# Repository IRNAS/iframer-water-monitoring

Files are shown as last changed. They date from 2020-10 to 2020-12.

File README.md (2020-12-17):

# Ifremer water monitoring

## Introduction

This repository contains all documentation and source code required to setup either a Inductive Conductivity CTZN sensor (marked on sensor as SN-PCTZB) or Optical Dissolved Oxygen OPTOD sensor (marked on sensor as SN-PODOC).
Sensors product page can be found on manufacturers [website][product_page].
The source code was written to work on [B-L072Z-LRWAN1][lora_board], while using Arduino core.

All manufacturers documentation can be found in `aqualabo_docs` folder.
Desktop application for measuring can be found in `aqualabo_software` folder.

## Prerequisites
* B-L072Z-LRWAN1
* Pira Smart RS485 Add-On board, documentation about it can be found in `rs485_addon_hardware` folder
* CTZN sensor or OPTOD sensor
* Arduino library for [Modbus protocol][arduino_library]
* Aqualabo 4200 Digital Module box, needed only for finding ModBus address and calibration.

<p align="center">
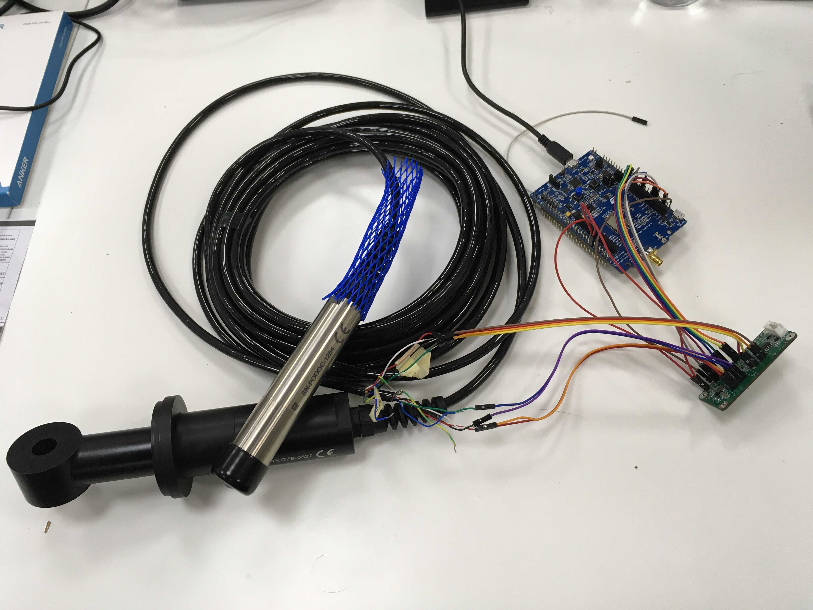
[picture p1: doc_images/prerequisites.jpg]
  <br><br>
  <i>Required setup</i><br>
</p>

[product_page]: https://en.aqualabo.fr/ctzn-digital-sensor-bare-wires-3-m-cable-stainless-steel-pipe-b4002.html
[lora_board]: https://www.st.com/en/evaluation-tools/b-l072z-lrwan1.html
[arduino_library]: https://github.com/4-20ma/ModbusMaster 

## Aqualabo sensors

This library currently supports two sensors:

* CTZN inductive conductivity sensor, address 50
* OPTOD optical oxygen sensor, address 10

## Finding ModBus address of the Aqualabo sensor

The best way to find address of Aqualabo sensor is to use Calsens software, installer for it can be found in `aqualabo_software` folder.
When using Calsens software the Aqualabo 4200 Digital Module box is required.

## Calibrating the Aqualabo sensor

To calibrate the Aqualabo sensor we have to use Calsens software, installer for it can be found in `aqualabo_software` folder.
Calibration procedure is described in user manuals of each specific sensors, as well as in `Modbus_Specifications_v021-EN.pdf` document.
When using Calsens software the Aqualabo 4200 Digital Module box is required.

## Wiring

There are two different wiring setups that need to be taken care of.

### Connections between Aqualabo sensor and Add-on board

As seen on image below Aqualabo sensor has 6 wires, wires numbers 2 (blue) and 6 (green/yellow) are not needed.
Aqualabo sensor has to be connected to one of two ports P1 or P2. Markings for Addon board can be seen on schematic below, there are also silkscreen markings on the bottom side of the board.

<p align="center">
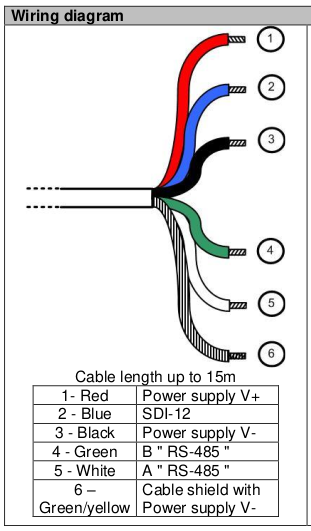
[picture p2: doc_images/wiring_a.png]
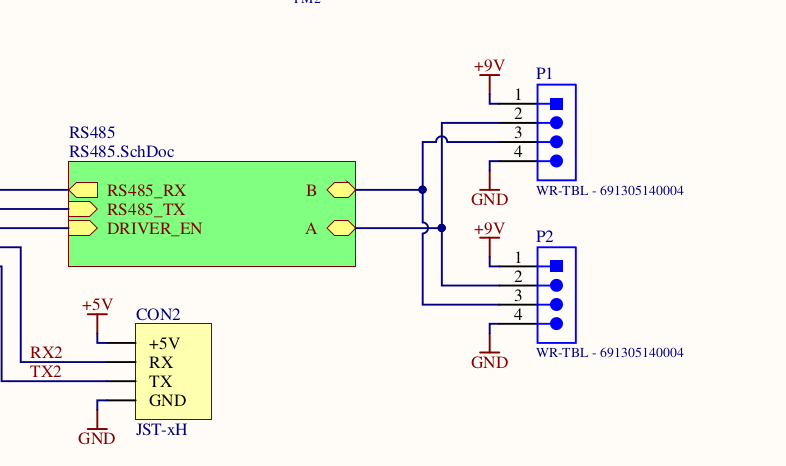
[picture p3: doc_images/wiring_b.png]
<br><br>
  <i>Wiring scheme of Aqualabo sensor and Add-on board</i><br>
</p>

### Connections between Add-on board and microcontroller

Connections are marked on image below, we need to provide following lines:
* 3.3V
* 5V
* GND
* TXD
* RXD
* GPIO18 (UART_SEL_B)
* GPIO23 (UART_SEL_A)
* GPIO24 (UART_INH)
* GPIO25 (DRIVER_EN)

**Important**: We actually do not need to switch UART lines when connection Add-on board to the microcontroller.
There is a mistake in naming in schematic and lines are already switched.
We therefore connect TX line from microcontroller to the TXD of Raspberry Pi header, same goes for RX and RXD.

<p align="center">
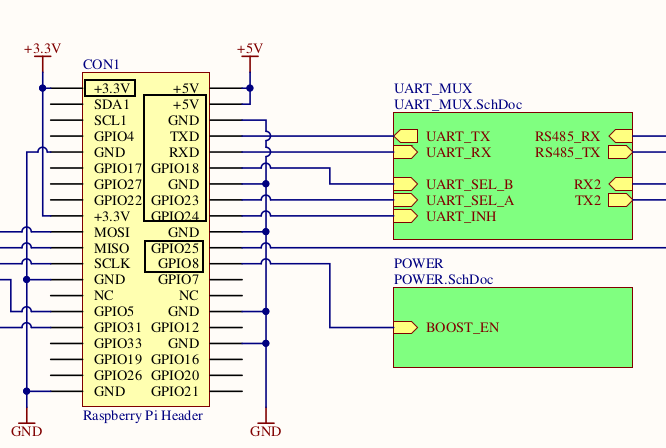
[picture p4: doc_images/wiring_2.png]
  <br><br>
  <i> Connections on Add-on board</i><br>
</p>

## Hardware changes on the Add-on board

There were some changes needed on the board to make communication possible.
This changes are not visible in schematic and are described here.

Changes:
* R7 0 ohm resistor should be placed
* R10 0 ohm resistor should not be placed
* R11 10 Kohm resistor should be replaced with 0 ohm resistor

Additional changes are needed to achieve low current consumption on Add-on V1 board:
* Remove chip U4 uart mux chip
* Connect together with a wire solder pads 1 and 3 left behind U4 chip.
* Connect together with a wire solder pads 12 and 13 left behind U4 chip.
* Solder on 3.3V low drop regulator and connect to its input 5V line, then connect to its output 3V line of the Add-on board.

For required connections refer to the image below.

<p align="center">
<br><br>
  <i> Low current consumption modifications on Add-on board</i><br>
</p>

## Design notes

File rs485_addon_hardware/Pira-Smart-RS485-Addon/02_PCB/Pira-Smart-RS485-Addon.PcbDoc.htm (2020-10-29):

Reporting Options

# File in Previous Format

Date | : | 16. 04. 2019
Time | : | 11:17:16
Filename | : | D:\OneDrive\IRNAS-Common\_NEW-IRNAS-COMMON\Pira-Smart-RS485-Addon\02_PCB\Pira-Smart-RS485-Addon.PcbDoc

Version | Warning

This file was generated by an earlier version of the software

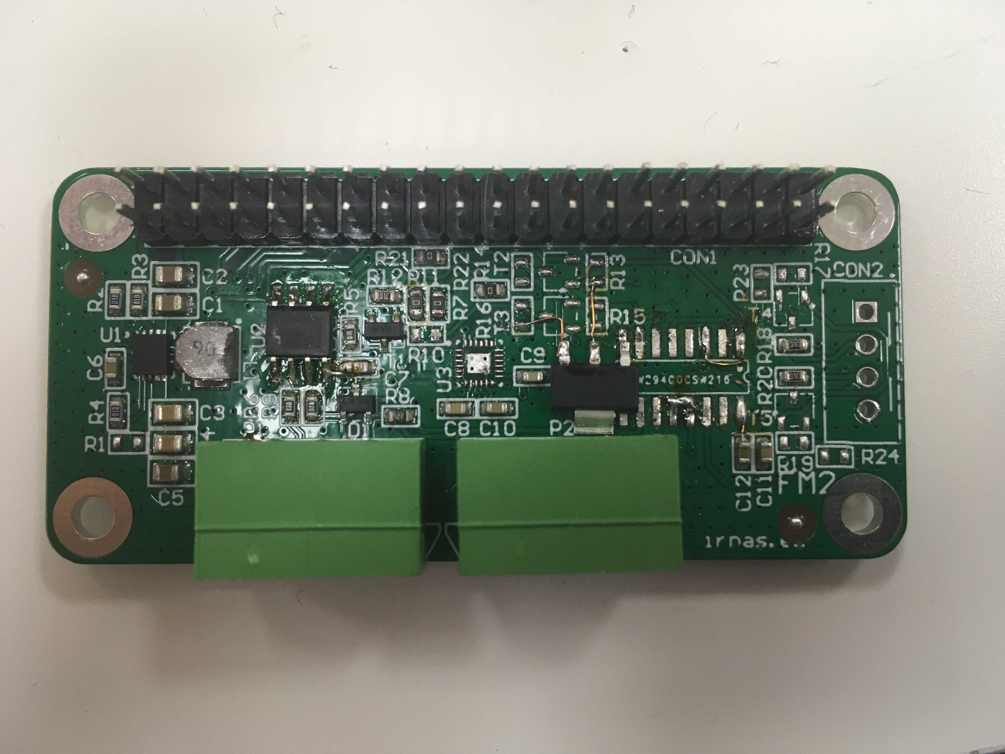
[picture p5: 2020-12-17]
doc_images/addon_modification.jpg

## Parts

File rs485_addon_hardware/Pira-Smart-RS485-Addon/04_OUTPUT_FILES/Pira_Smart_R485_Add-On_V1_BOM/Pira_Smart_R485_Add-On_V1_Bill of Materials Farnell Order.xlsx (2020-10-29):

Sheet: Altium Output
Supplier Part Number 1 | Quantity | Description | Designator | Supplier 1 | IRNAS Part No.
1824869 | 1 | TVS Diode, CDSOT23 Series, Bidirectional, 12 V, 26 V, SOT-23, 3 Pins | D1 | Farnell
2530091 | 1 | MURATA - FDSD0420-H-1R5M=P3 - INDUCTOR, SHIELDED, 1.5UH, 5.1A, 20% | L1 | Farnell
2073357 | 1 | MULTICOMP - MCMR06X104 JTL - RES, CERAMIC, 1M02, 1%, 0.1W, 0603 | R1 | Farnell
1738892 | 1 | RES SMD 120 OHM 1% 1/4W 0603 | R8 | Farnell
9845321 | 3 | N-Channel Vds = 100V, Id = 170 mA | T1, T4, T5 | Farnell
595-TPS63070RNMR | 1 | TEXAS INSTRUMENTS - TPS63070RNMT - DC/DC CONV, BUCK-BOOST, 2.4MHZ, VQFN-15 | U1 | Mouser
2335547 | 1 | Transceiver RS485 Driver, 3V-3.6V supply, SOIC-8 | U2 | Farnell
410-MPU-9250 | 1 | IMU ACCEL/GYRO/MAG I2C/SPI 24QFN | U3 | Mouser
2854627 | 1 | Analog Multiplexer/Demultiplexer, 4:1, 2 Circuits, 100ohm, 2V to 5.5V Supply, SOIC-16 | U4 | Farnell

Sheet: Farnell Order
Supplier Part Number 1 | Quantity | Description | Designator | No. PCBs | Material in stock
#REF! | #REF! | #REF! | #REF!
#REF! | #REF! | #REF! | #REF!
#REF! | #REF! | #REF! | #REF!
#REF! | #REF! | #REF! | #REF!
#REF! | #REF! | #REF! | #REF!
#REF! | #REF! | #REF! | #REF!
#REF! | #REF! | #REF! | #REF!
1824869 | 0 | TVS Diode, CDSOT23 Series, Bidirectional, 12 V, 26 V, SOT-23, 3 Pins | D1
2530091 | 0 | MURATA - FDSD0420-H-1R5M=P3 - INDUCTOR, SHIELDED, 1.5UH, 5.1A, 20% | L1
2073357 | 0 | MULTICOMP - MCMR06X104 JTL - RES, CERAMIC, 1M02, 1%, 0.1W, 0603 | R1
#REF! | #REF! | #REF! | #REF!
#REF! | #REF! | #REF! | #REF!
1738892 | 0 | RES SMD 120 OHM 1% 1/4W 0603 | R8
#REF! | #REF! | #REF! | #REF!
9845321 | 0 | N-Channel Vds = 100V, Id = 170 mA | T1, T4, T5
595-TPS63070RNMR | 0 | TEXAS INSTRUMENTS - TPS63070RNMT - DC/DC CONV, BUCK-BOOST, 2.4MHZ, VQFN-15 | U1
2335547 | 0 | Transceiver RS485 Driver, 3V-3.6V supply, SOIC-8 | U2
410-MPU-9250 | 0 | IMU ACCEL/GYRO/MAG I2C/SPI 24QFN | U3
2854627 | 0 | Analog Multiplexer/Demultiplexer, 4:1, 2 Circuits, 100ohm, 2V to 5.5V Supply, SOIC-16 | U4
0 | 0 | 0 | 0
0 | 0 | 0 | 0
0 | 0 | 0 | 0
0 | 0 | 0 | 0
0 | 0 | 0 | 0
0 | 0 | 0 | 0
0 | 0 | 0 | 0
0 | 0 | 0 | 0
0 | 0 | 0 | 0
0 | 0 | 0 | 0
0 | 0 | 0 | 0
0 | 0 | 0 | 0
0 | 0 | 0 | 0
0 | 0 | 0 | 0
0 | 0 | 0 | 0
0 | 0 | 0 | 0
0 | 0 | 0 | 0
0 | 0 | 0 | 0
0 | 0 | 0 | 0
0 | 0 | 0 | 0
0 | 0 | 0 | 0
0 | 0 | 0 | 0
0 | 0 | 0 | 0
0 | 0 | 0 | 0
0 | 0 | 0 | 0
0 | 0 | 0 | 0
0 | 0 | 0 | 0
0 | 0 | 0 | 0
0 | 0 | 0 | 0
0 | 0 | 0 | 0
0 | 0 | 0 | 0
0 | 0 | 0 | 0
0 | 0 | 0 | 0
0 | 0 | 0 | 0
0 | 0 | 0 | 0
0 | 0 | 0 | 0
0 | 0 | 0 | 0
0 | 0 | 0 | 0
0 | 0 | 0 | 0
0 | 0 | 0 | 0
0 | 0 | 0 | 0
0 | 0 | 0 | 0
0 | 0 | 0 | 0
0 | 0 | 0 | 0
0 | 0 | 0 | 0
0 | 0 | 0 | 0
0 | 0 | 0 | 0
0 | 0 | 0 | 0
0 | 0 | 0 | 0
0 | 0 | 0 | 0
0 | 0 | 0 | 0
0 | 0 | 0 | 0
0 | 0 | 0 | 0
0 | 0 | 0 | 0
0 | 0 | 0 | 0
0 | 0 | 0 | 0
0 | 0 | 0 | 0
0 | 0 | 0 | 0
0 | 0 | 0 | 0
0 | 0 | 0 | 0
0 | 0 | 0 | 0
0 | 0 | 0 | 0
0 | 0 | 0 | 0
0 | 0 | 0 | 0
0 | 0 | 0 | 0
0 | 0 | 0 | 0
0 | 0 | 0 | 0
0 | 0 | 0 | 0
0 | 0 | 0 | 0
0 | 0 | 0 | 0
0 | 0 | 0 | 0
0 | 0 | 0 | 0
0 | 0 | 0 | 0
0 | 0 | 0 | 0
0 | 0 | 0 | 0
0 | 0 | 0 | 0
0 | 0 | 0 | 0
0 | 0 | 0 | 0
0 | 0 | 0 | 0
0 | 0 | 0 | 0

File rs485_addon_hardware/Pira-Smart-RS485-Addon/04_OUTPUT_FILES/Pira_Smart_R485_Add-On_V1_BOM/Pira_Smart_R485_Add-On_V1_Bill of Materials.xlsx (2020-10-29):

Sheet: Part List Report
 | Component list |  |  | Pira_Smart_R485_Add-On
 | Source Data From: | Pira_Smart_RS485_Addon.PrjPCB |  |  | Contact:
 | Project: | Pira_Smart_RS485_Addon.PrjPCB
 | Variant: | BASIC |  |  |  |  |  |  | IRNAS
 | Report Date: | 25. 04. 2019 | 15:00:00 |  |  |  |  |  | www.irnas.eu
 | Print Date: | 2019-04-25 | 43580.62533
# | Manufacturer Part Number 1 | Manufacturer 1 | Description | Footprint | Designator | Quantity | Supplier 1 | Supplier Part Number 1 | Supplier Order Qty 1 | Supplier Stock 1 | Supplier Unit Price 1 | Supplier Subtotal 1 | Supplier Currency 1
1 |  |  | Serie 3051 - 3.50mm Horizontal PCB Header with Plastic Latch WR-TBL, 4 pin | 691305140004 | P1, P2 | 2
2 |  |  | KEMET - C0603X103K5RECAUTO - CAP, MLCC, AEC-Q200, X7R, 0.01UF, 50V | CAP0603 | C9 | 1 | Farnell | 2760492
3 |  |  | MURATA - GRM188R61H105KAALD - CAP, MLCC, X5R, 1UF, 50V, 0603 | CAP0603 | C12 | 1 | Farnell | 1845736
4 |  |  | MURATA - GRM188R71C104KA01J - CAP, MLCC, X7R, 0.1UF, 16V, 0603 | CAP0603 | C6, C7, C8, C10, C11 | 5 | Farnell | 2688519
5 |  |  | MULTICOMP - MC0805X226M6R3CT - CAP, MLCC, X5R, 22UF, 0805 | CAP0805 | C3, C4 | 2 | Farnell | 1759415
6 |  |  | TDK - CGA4J1X5R1C106K125AC - CAP, MLCC, X5R, 10UF, 16V, 0805 | CAP0805 | C1, C2, C5 | 3 | Farnell | 2210948RL
7 |  |  | MURATA - FDSD0420-H-1R5M=P3 - INDUCTOR, SHIELDED, 1.5UH, 5.1A, 20% | FDSD0402 | L1 | 1 | Farnell | 2530091
8 |  |  | FIDUCAL MARKER | FIDUCAL | FM1, FM2 | 2
9 |  |  | Header, 20-Pin, Dual row | HDR2X20 | CON1 | 1
10 |  |  | 4 Positions Header, Shrouded Connector 0.098" (2.50mm) Through Hole Tin | JST-xH | CON2 | 1 | Farnell | 1516278
11 |  |  | IMU ACCEL/GYRO/MAG I2C/SPI 24QFN | QFN40P300X300X105_HS-25N | U3 | 1 | RSComponents | 883-7942P
12 |  |  | BOURNS - CR0603-J/-000ELF - RES, THICK FILM, 0R, 5%, 0.1W, 0603 | RES0603 | R10, R21, R22 | 3 | Farnell | 2008343
13 |  |  | MULTICOMP - MCMR06X103 JTL - RES, CERAMIC, 10K, 5%, 0.1W, 0603 | RES0603 | R5, R11, R12, R17, R18, R19, R20 | 7 | Farnell | 2073356
14 |  |  | MULTICOMP - MCMR06X104 JTL - RES, CERAMIC, 1M02, 1%, 0.1W, 0603, MULTICOMP - MCMR06X104 JTL - RES, CERAMIC, 100K, 5%, 0.1W, 0603, MULTICOMP - MCMR06X104 JTL - RES, CERAMIC, 100K, 1%, 0.1W, 0603 | RES0603 | R1, R2, R3, R4 | 4 | Farnell | 2073357
15 |  |  | RES SMD 120 OHM 1% 1/4W 0603 | RES0603 | R8 | 1 | Farnell | 1738892
16 |  |  | VISHAY - RCA060310R0FKEA - RES, AUTO, THICK FILM, 10R, 1%, 0603 | RES0603 | R6, R9 | 2 | Farnell | 2616585
17 |  |  |  | SOIC-8 REFLOW | U2 | 1 | Farnell | 2335547
18 |  |  | Analog Multiplexer/Demultiplexer, 4:1, 2 Circuits, 100ohm, 2V to 5.5V Supply, SOIC-16 | SOIC-16 | U4 | 1 | Farnell | 2854627
19 |  |  | N-Channel Vds = 100V, Id = 170 mA | SOT23-3AL | T1, T4, T5 | 3 | Farnell | 9845321
20 |  |  | TVS Diode, CDSOT23 Series, Bidirectional, 12 V, 26 V, SOT-23, 3 Pins | SOT23-3AL | D1 | 1 | Farnell | 1776392
21 |  |  | TEXAS INSTRUMENTS - TPS63070RNMT - DC/DC CONV, BUCK-BOOST, 2.4MHZ, VQFN-15 | VQFN TPS | U1 | 1 | Mouser | 595-TPS63070RNMR
 |  |  |  |  |  | 44 |  |  | 0 |  |  | 0
Approved |  |  |  | Notes
 |  |  |  | pcs: |  | 20 |  | Total |  | 0 |  | <none>
 |  |  |  |  |  |  |  | Price for 1pcs |  | 0.00 |  | <none>

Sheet: Project Information
Project Full Path | D:\OneDrive\IRNAS-Common\_NEW-IRNAS-COMMON\Pira-Smart-RS485-Addon\Pira_Smart_RS485_Addon.PrjPCB
Project Filename | Pira_Smart_RS485_Addon.PrjPCB
Variant Name | BASIC
Data-Source Filename | Pira_Smart_RS485_Addon.PrjPCB
Data-Source Full Path | D:\OneDrive\IRNAS-Common\_NEW-IRNAS-COMMON\Pira-Smart-RS485-Addon\Pira_Smart_RS485_Addon.PrjPCB
Title | Bill of Materials for Variant [BASIC] of Project [Pira_Smart_RS485_Addon.PrjPCB] (No PCB Document Selected)
Total Quantity | 44
Report Time | 15:00:00
Report Date | 25. 04. 2019
Report Date & Tine | 25. 04. 2019 15:00
Output Name | Bill of Materials
Output Type | BOM_PartType
Output Generator Name | BOM
Output Generator Description | Bill of Materials

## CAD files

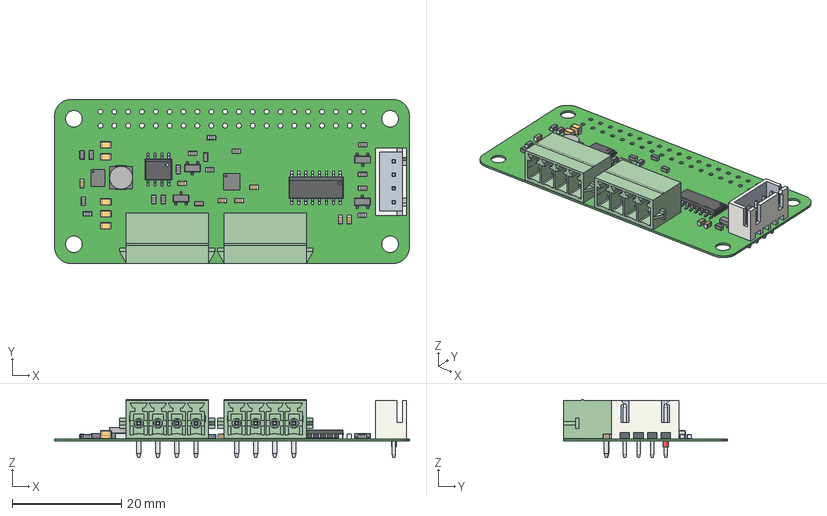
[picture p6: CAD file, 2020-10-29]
rs485_addon_hardware/Pira-Smart-RS485-Addon/04_OUTPUT_FILES/Pira_Smart_R485_Add-On_V1_3D/Pira_Smart_R485_Add-On_V1_3D STEP.step
65.1 x 30.1 x 10.7 mm
R0603 x 17
SW3DPS-SO-8_(PIC12FXXX)-DEFAULT
6913051400xx_PIN x 8
User_Library-soic16-1
Open_CASCADE_STEP_translator_6.8_1.1
Open_CASCADE_STEP_translator_6.8_1.2.1
Thermal_Shape
Open_CASCADE_STEP_translator_6.8_1.4.1 x 24
3-lead_sot23-3 x 4
SW3dPS-jst-b4b-xh-a-1
C_SMD_0603 x 7
Open_CASCADE_STEP_translator_6.8_4.1
Open_CASCADE_STEP_translator_6.8_4.2.1
Open_CASCADE_STEP_translator_6.8_4.3.1 x 16
Open_CASCADE_STEP_translator_6.8_2.3.1 x 2
CAPC2012X95N_EIA_0805 x 10

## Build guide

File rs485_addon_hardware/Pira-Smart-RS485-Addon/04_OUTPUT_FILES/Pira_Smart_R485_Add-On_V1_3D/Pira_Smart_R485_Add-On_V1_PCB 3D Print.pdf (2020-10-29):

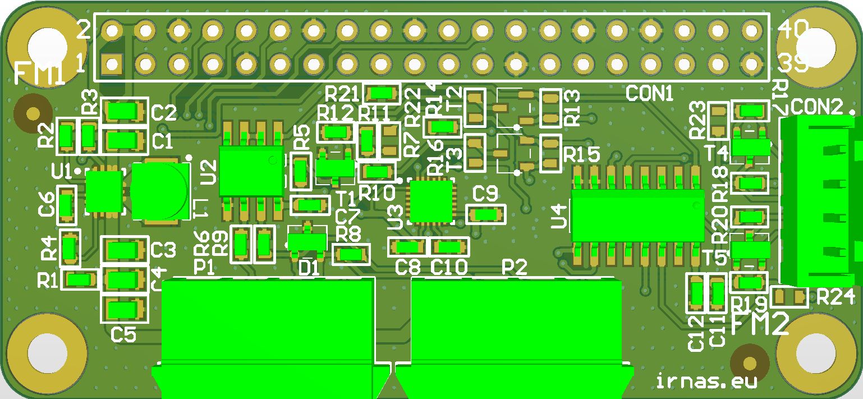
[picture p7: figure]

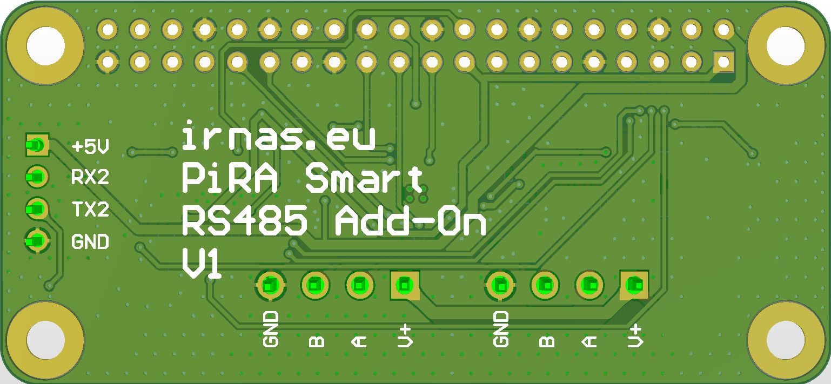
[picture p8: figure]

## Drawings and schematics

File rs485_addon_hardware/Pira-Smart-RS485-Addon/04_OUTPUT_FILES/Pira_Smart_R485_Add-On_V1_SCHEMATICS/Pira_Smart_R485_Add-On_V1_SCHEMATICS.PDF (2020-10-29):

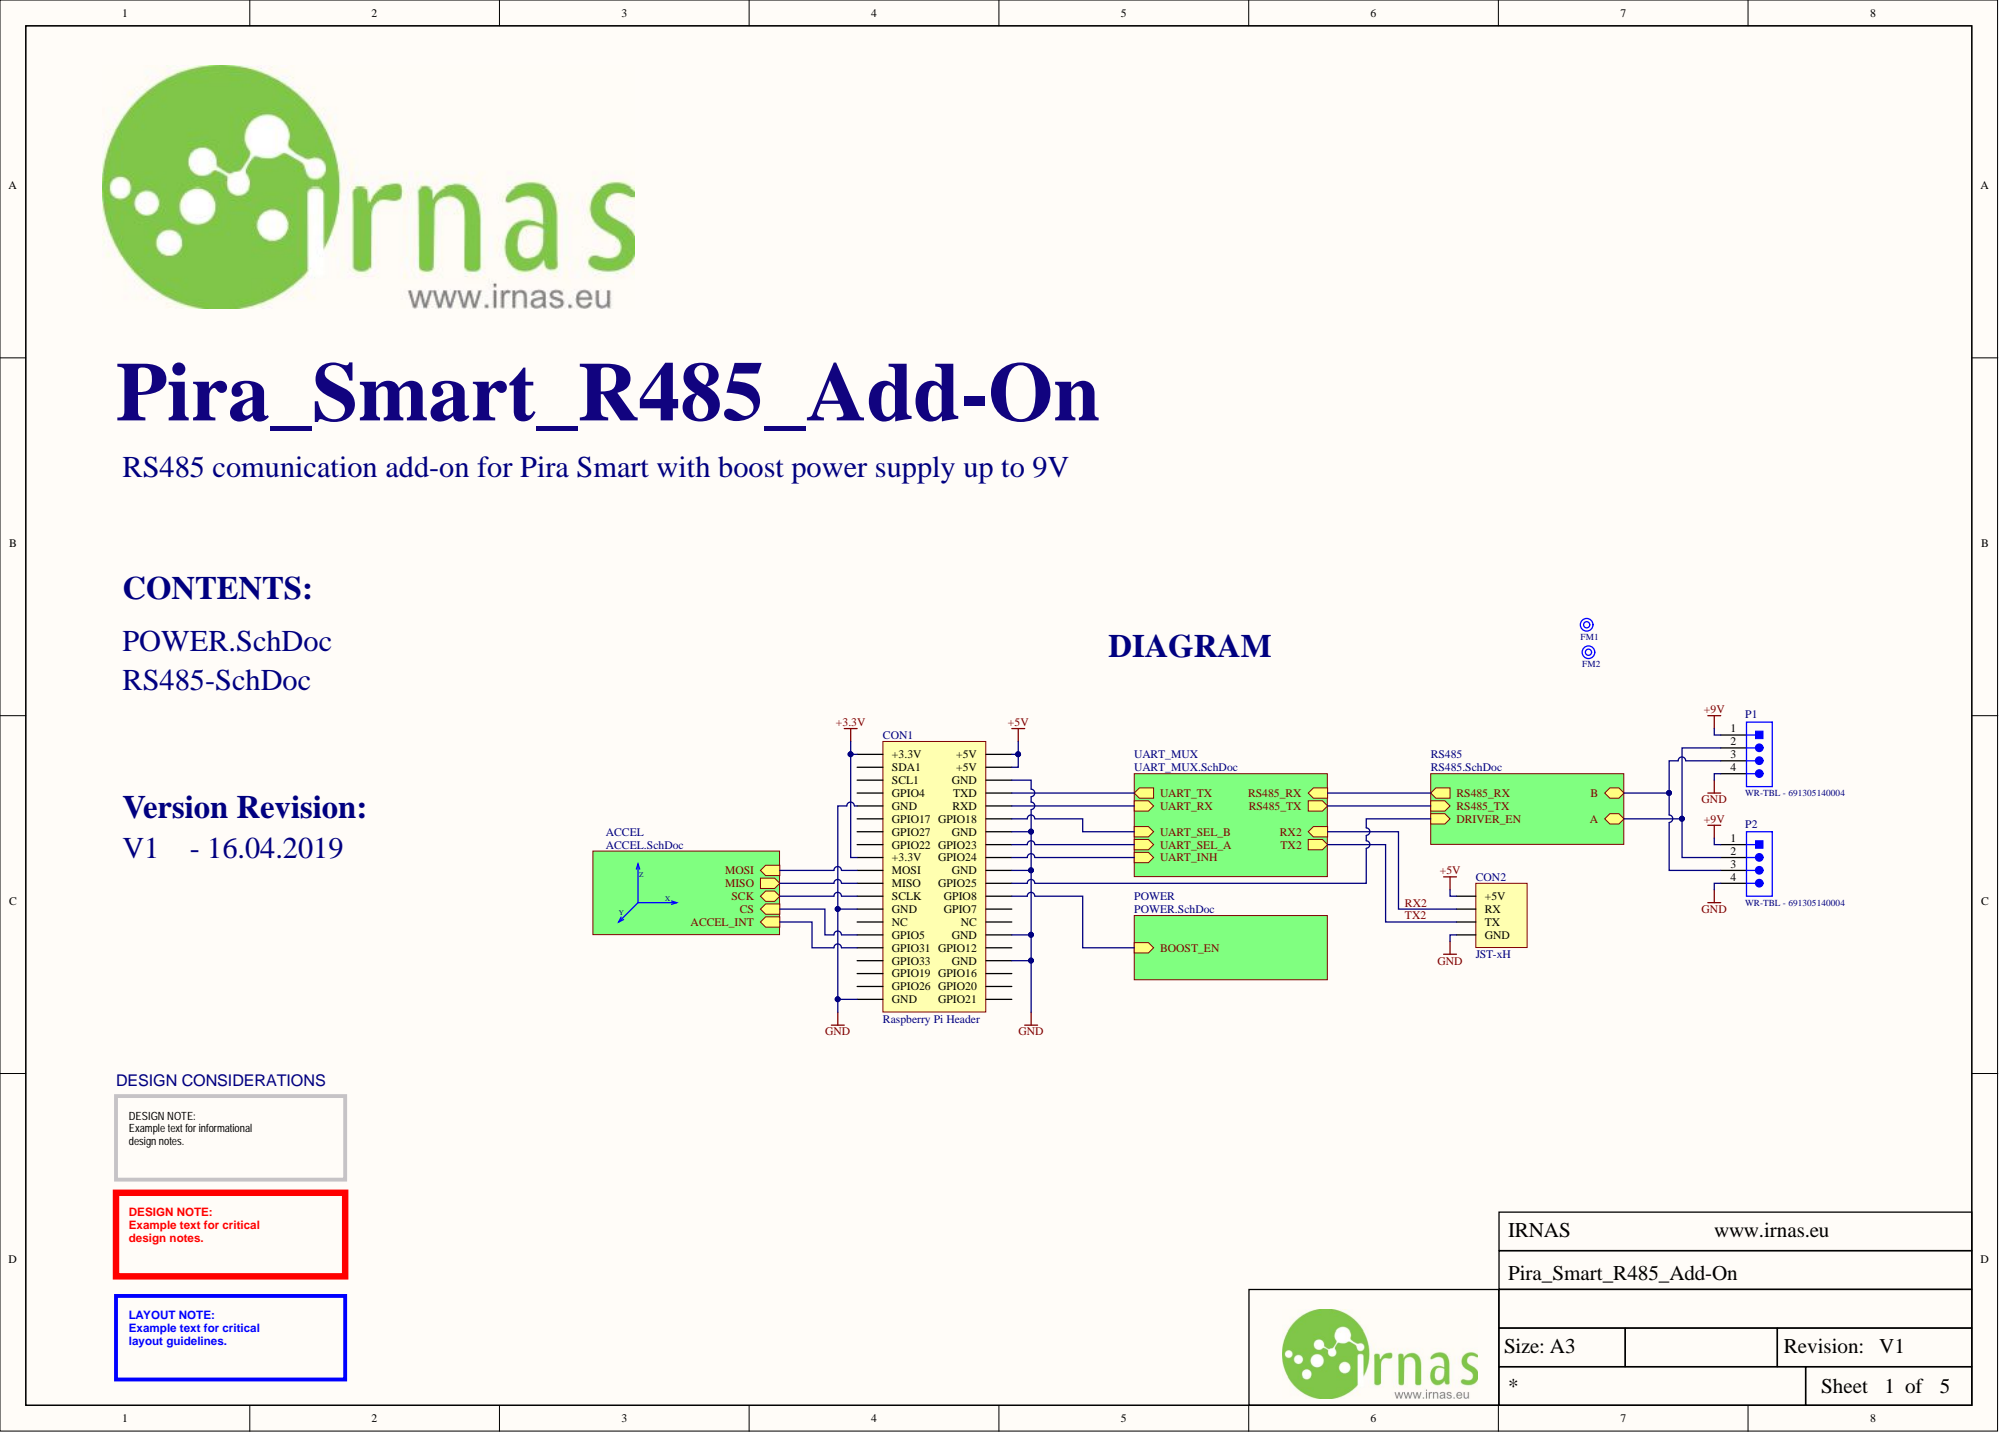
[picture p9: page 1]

RS485 comunication add-on for Pira Smart with boost power supply up to 9V

DESIGN NOTE:
Example text for informational
design notes.

Example text for critical

LAYOUT NOTE:
layout guidelines.

Size: A3 | | Revision: V1

* | Sheet of

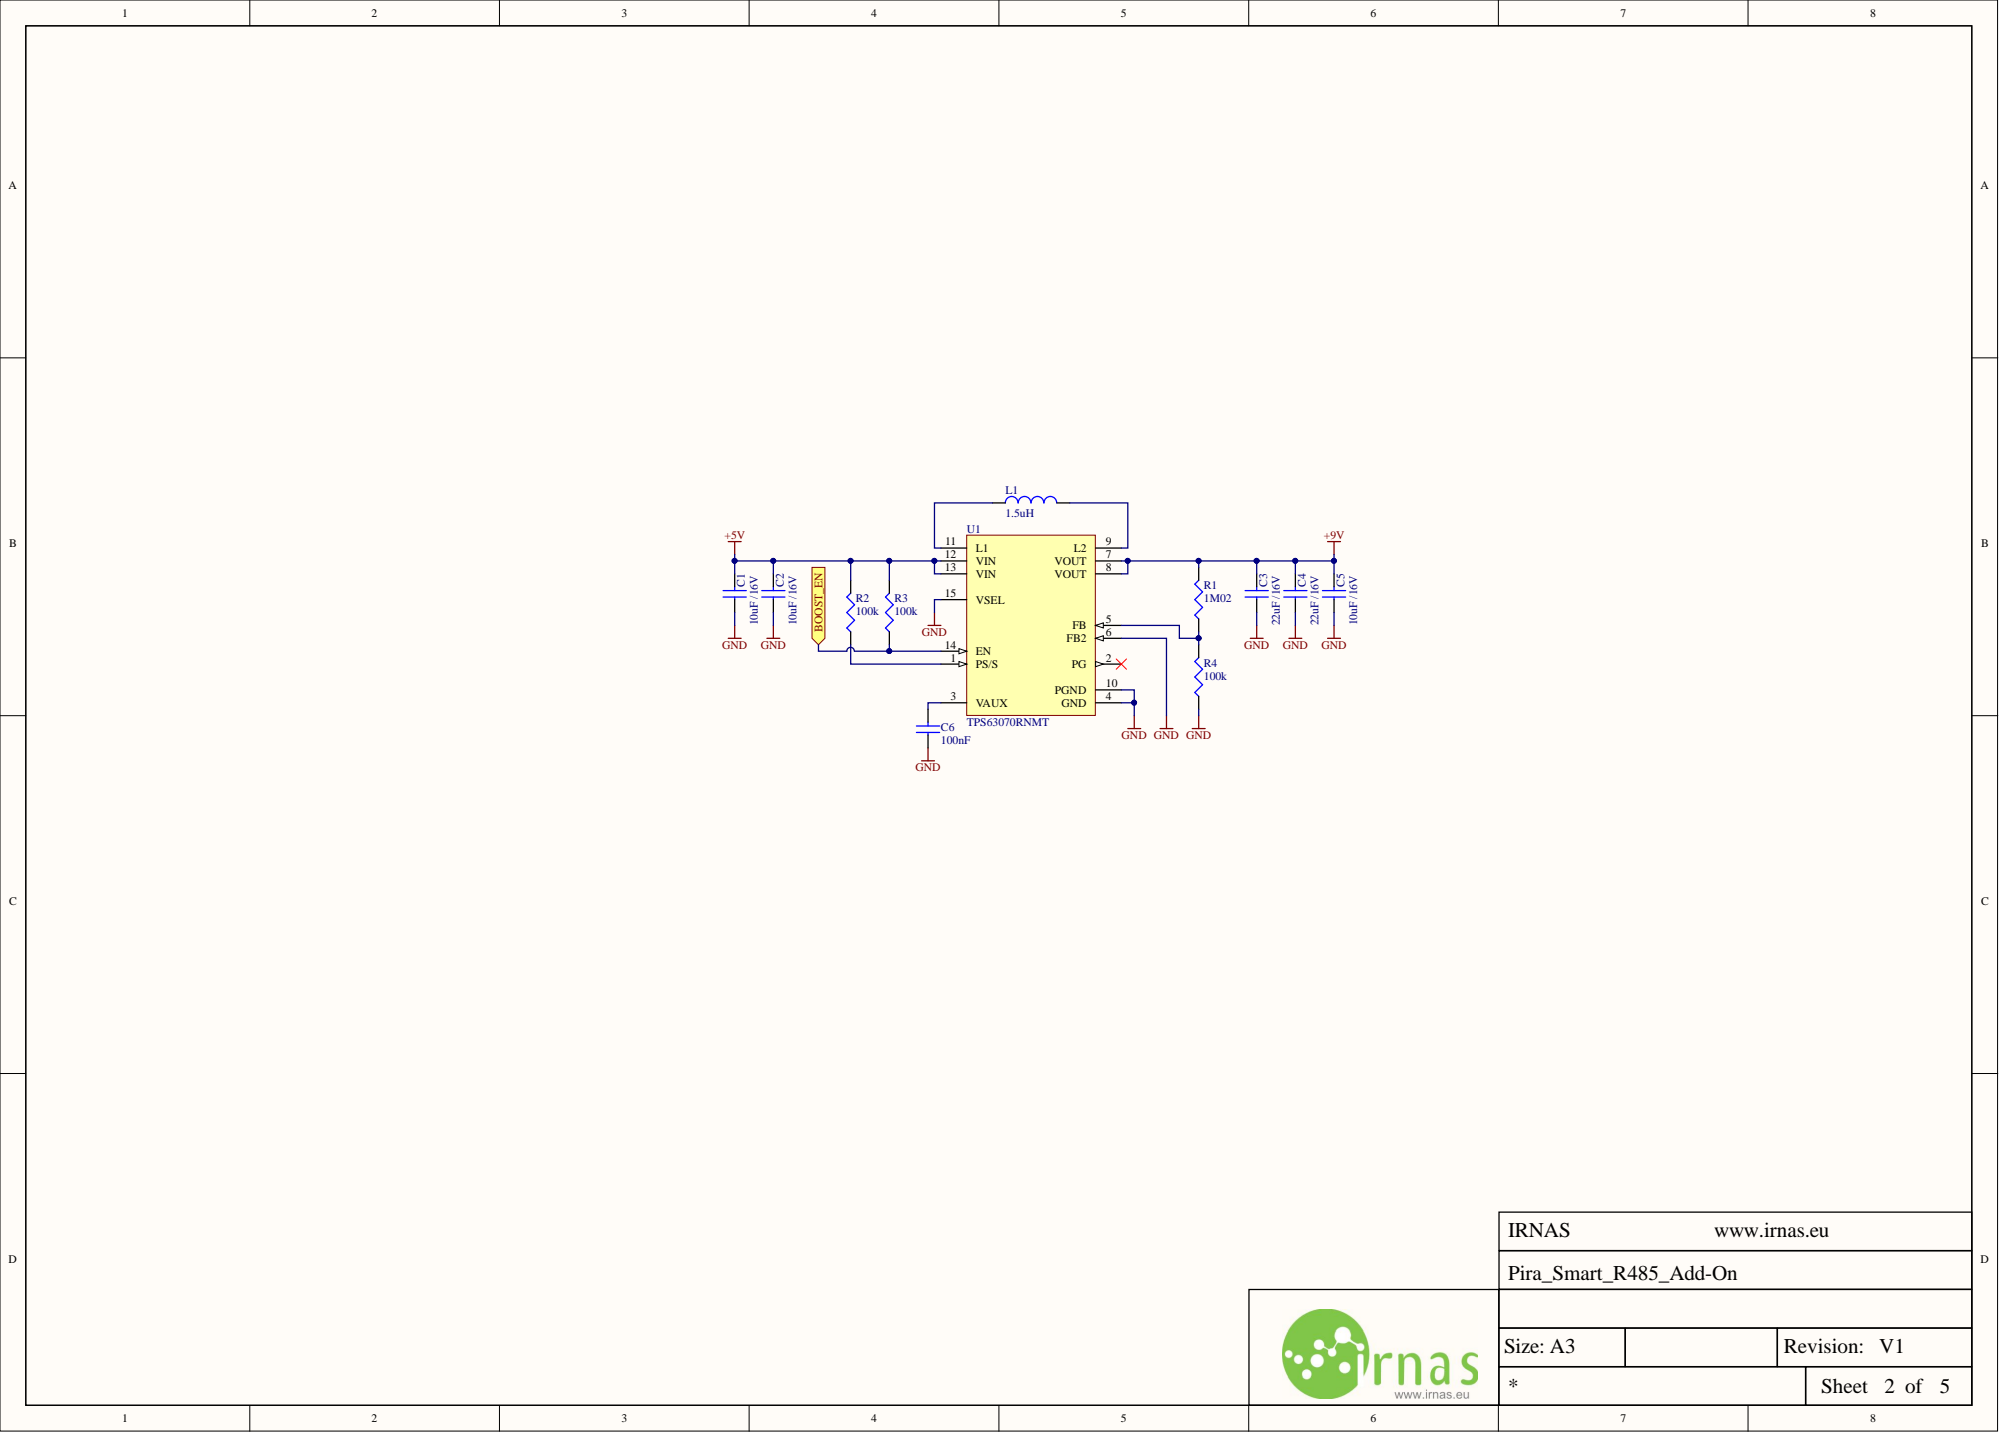
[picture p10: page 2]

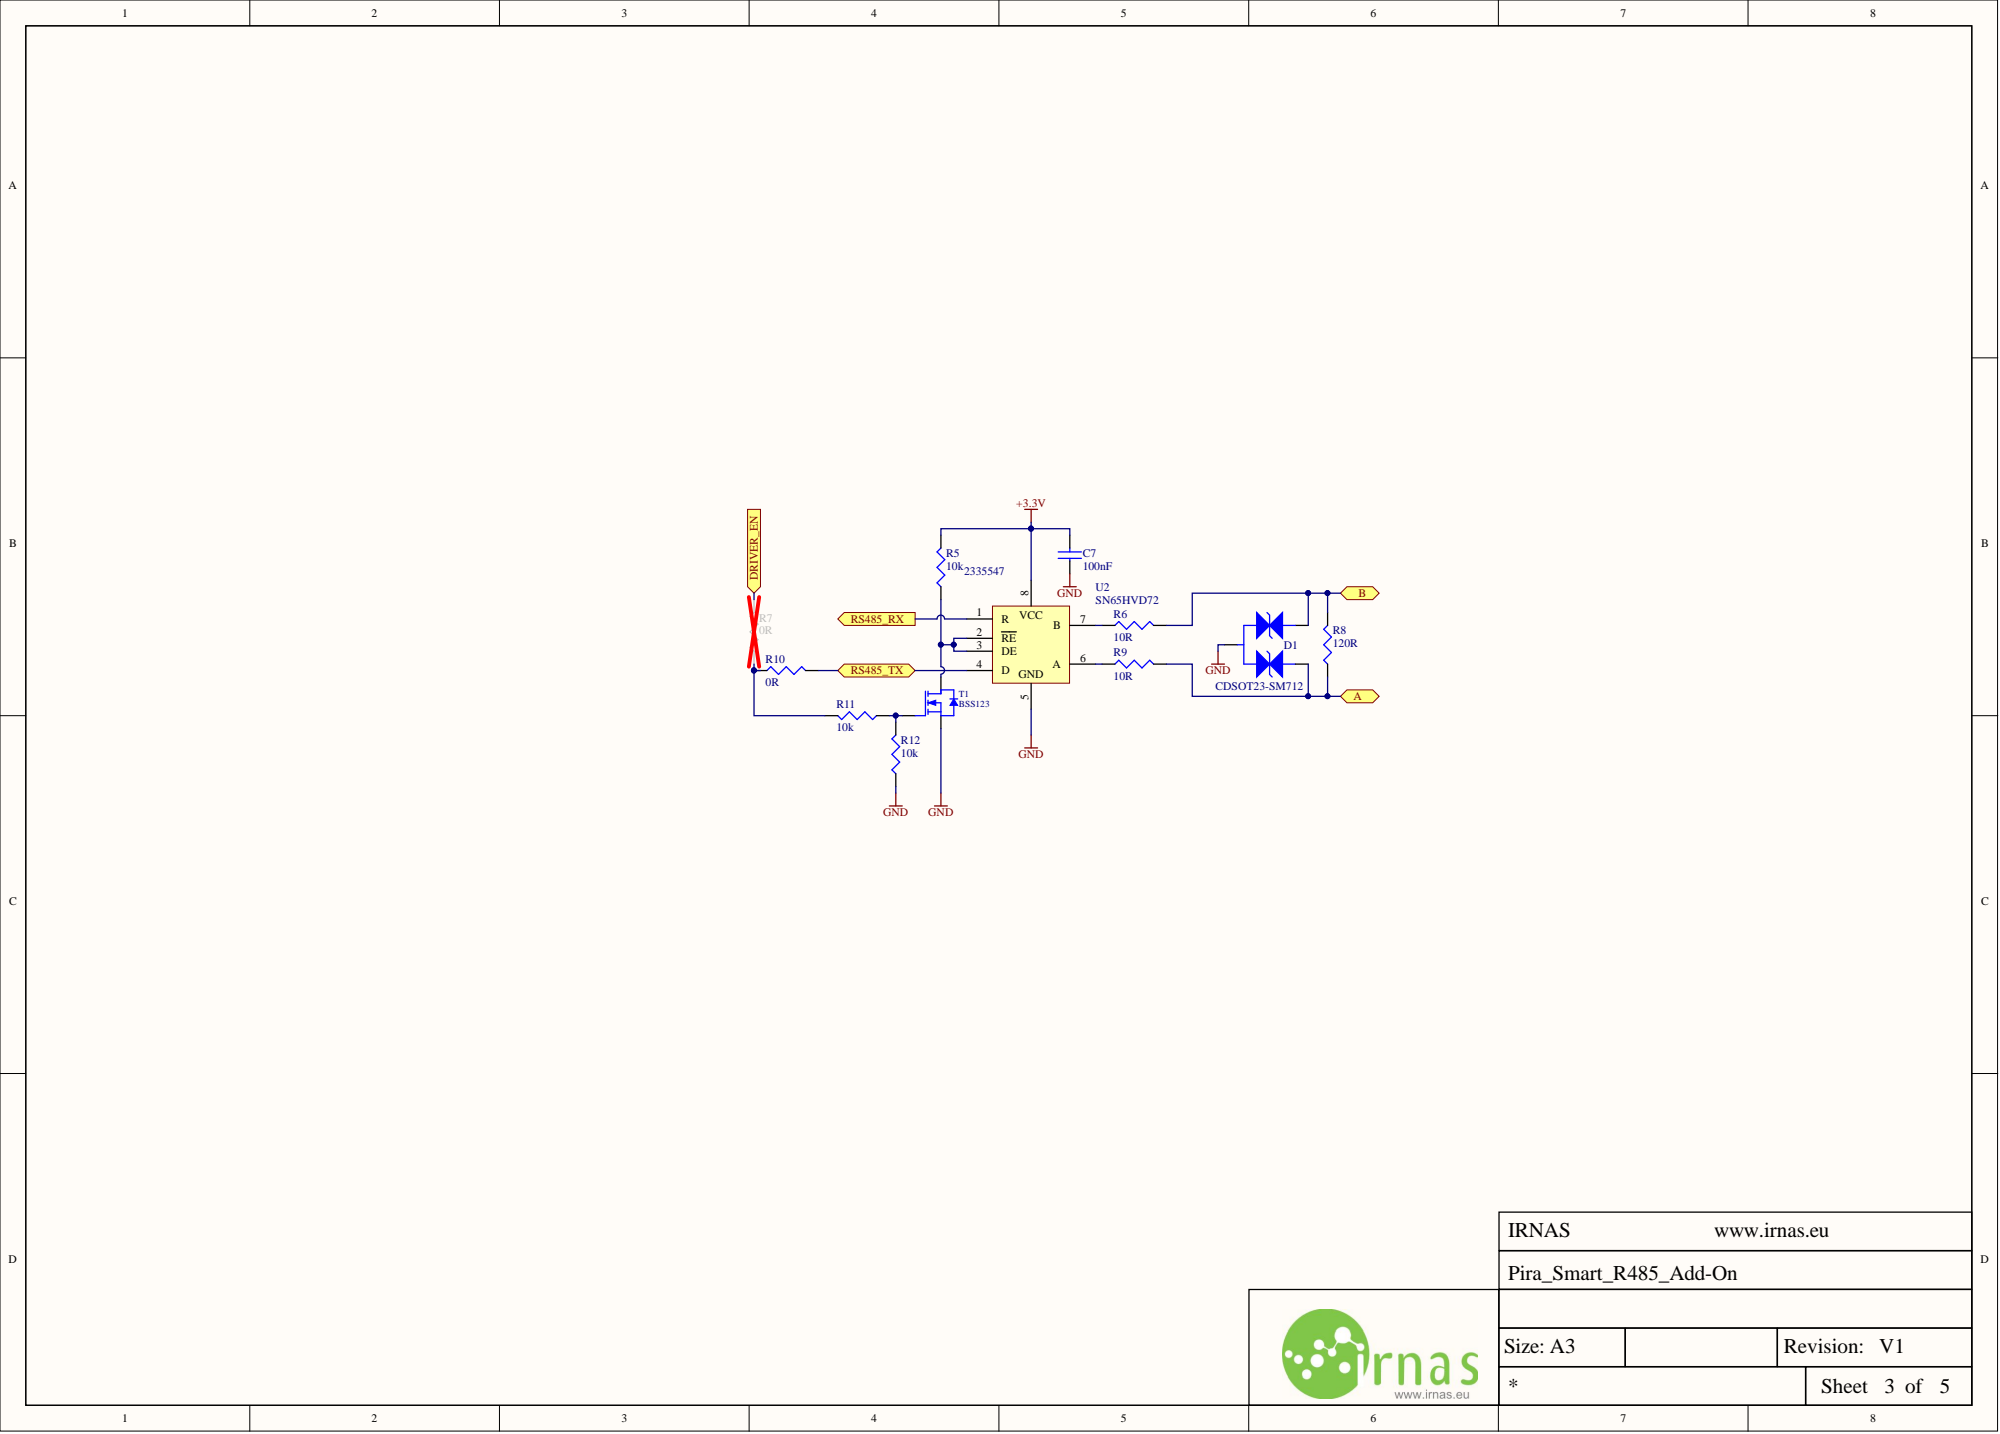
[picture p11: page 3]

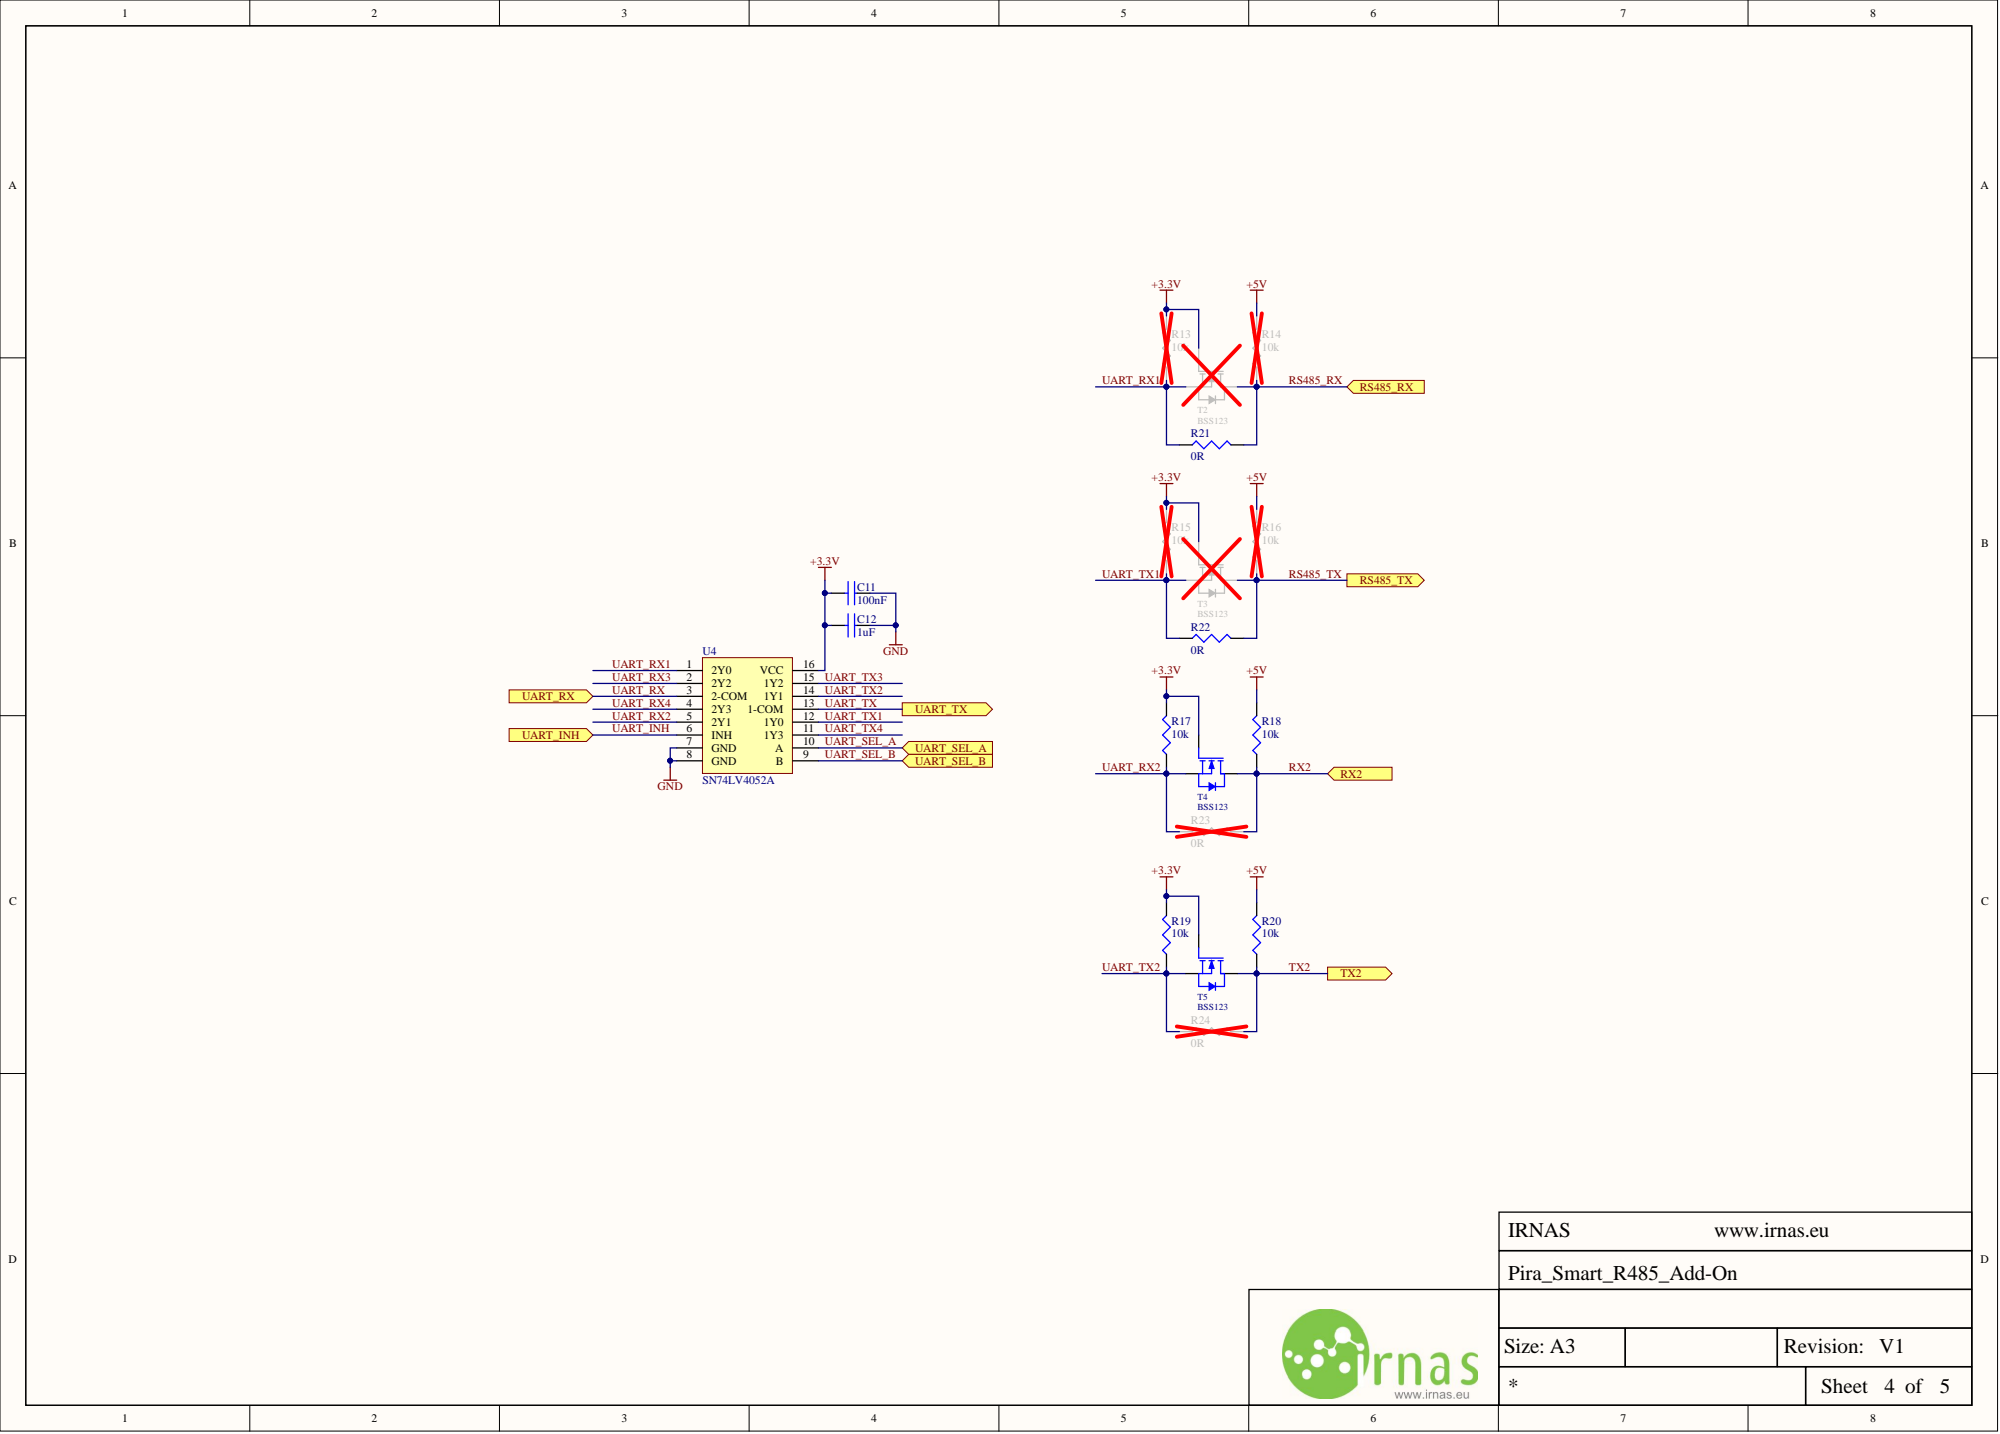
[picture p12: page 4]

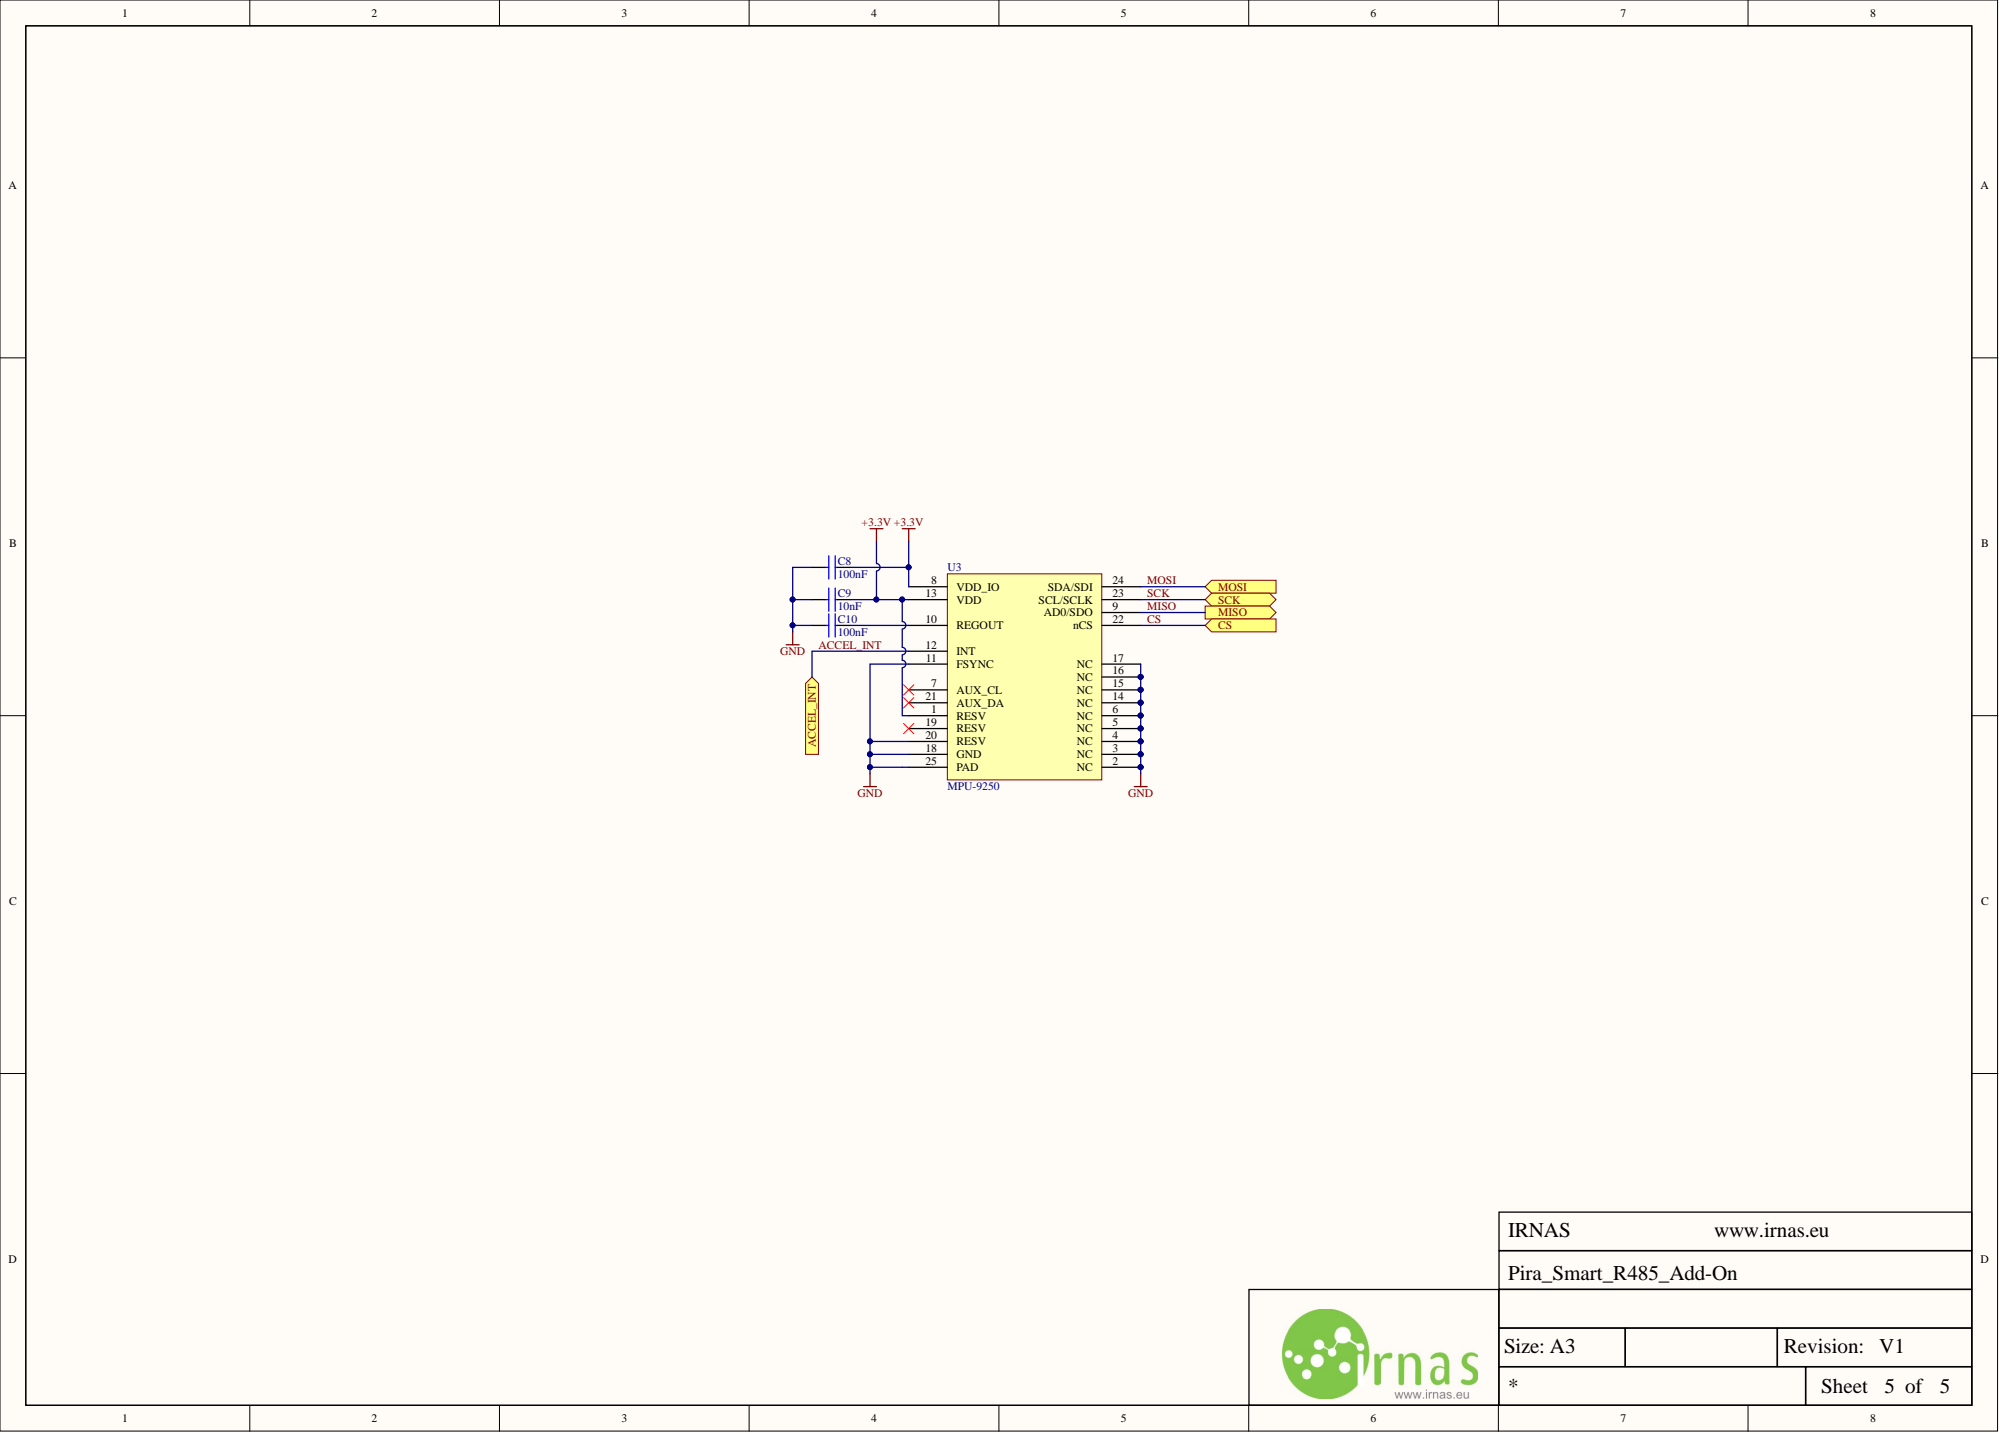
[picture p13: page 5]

RESV 19 | 2 NC 3 NC 4 NC 5 NC 6

GND 18
PAD 25

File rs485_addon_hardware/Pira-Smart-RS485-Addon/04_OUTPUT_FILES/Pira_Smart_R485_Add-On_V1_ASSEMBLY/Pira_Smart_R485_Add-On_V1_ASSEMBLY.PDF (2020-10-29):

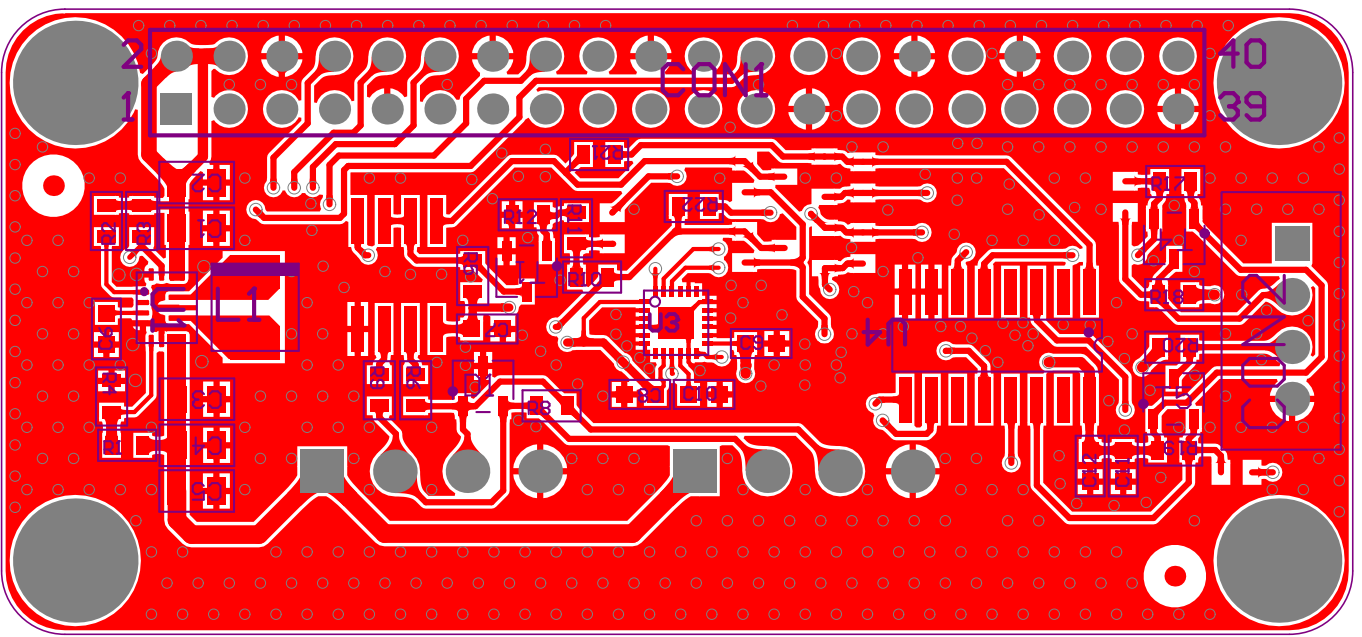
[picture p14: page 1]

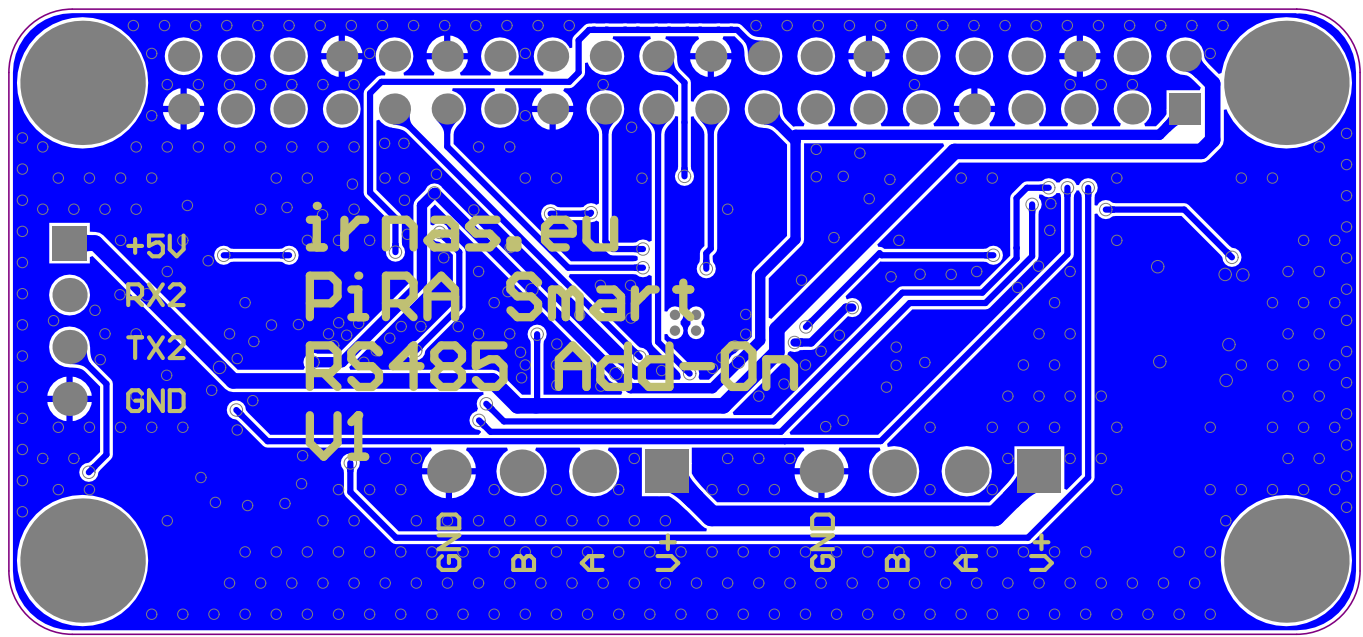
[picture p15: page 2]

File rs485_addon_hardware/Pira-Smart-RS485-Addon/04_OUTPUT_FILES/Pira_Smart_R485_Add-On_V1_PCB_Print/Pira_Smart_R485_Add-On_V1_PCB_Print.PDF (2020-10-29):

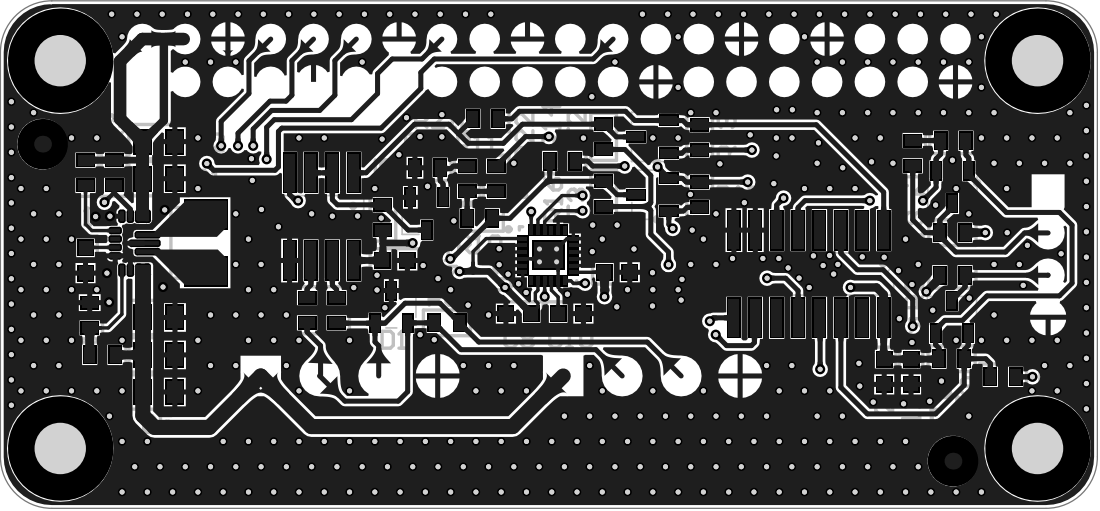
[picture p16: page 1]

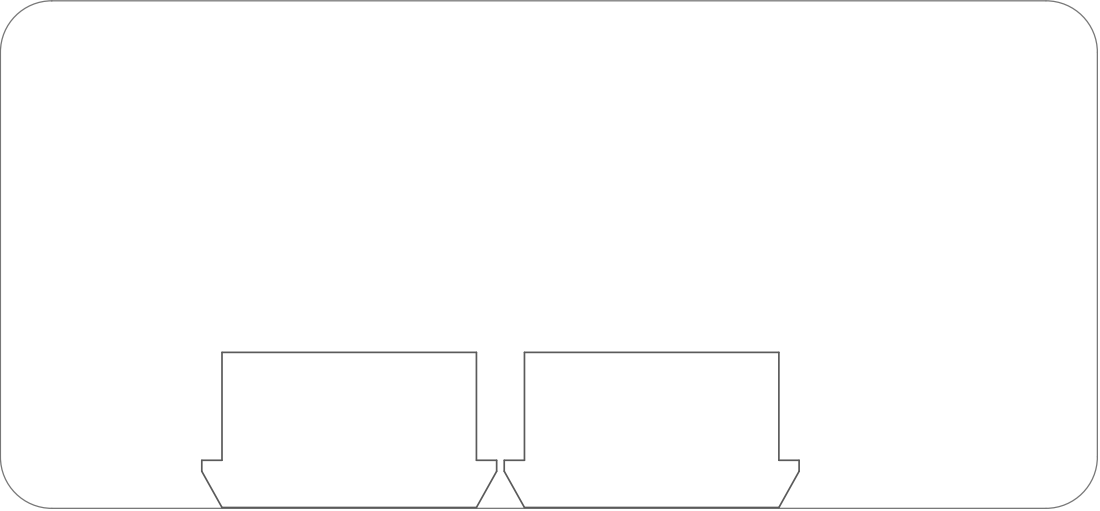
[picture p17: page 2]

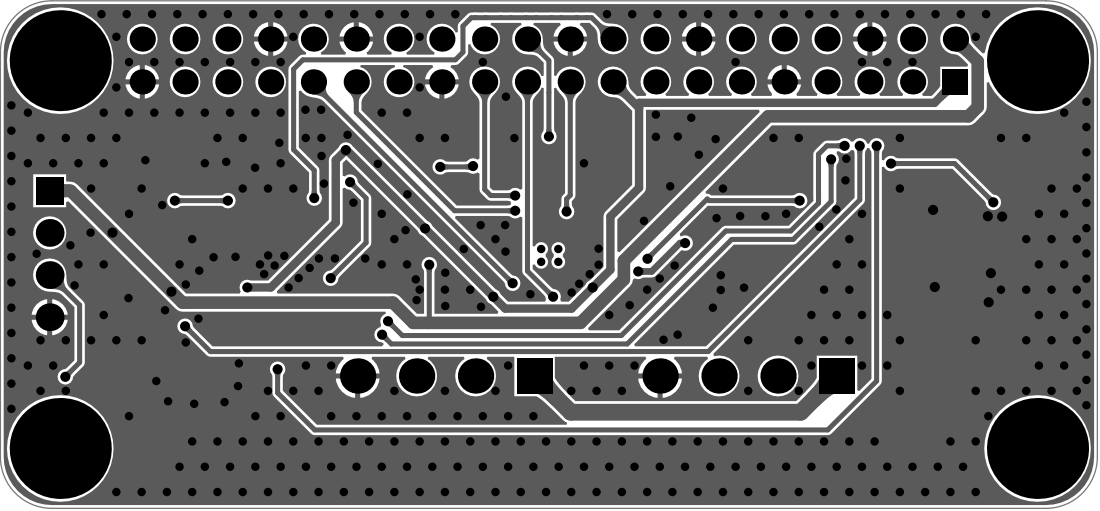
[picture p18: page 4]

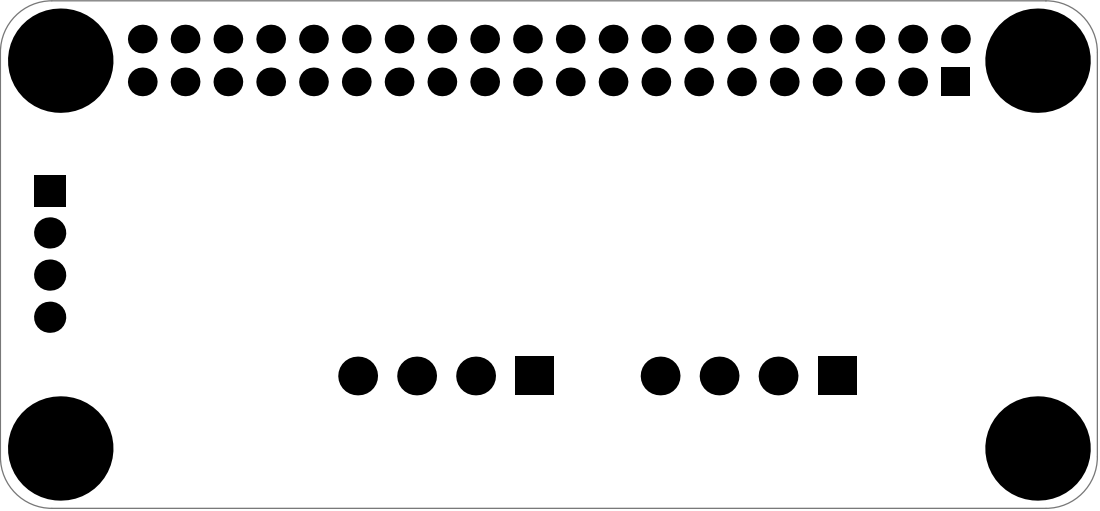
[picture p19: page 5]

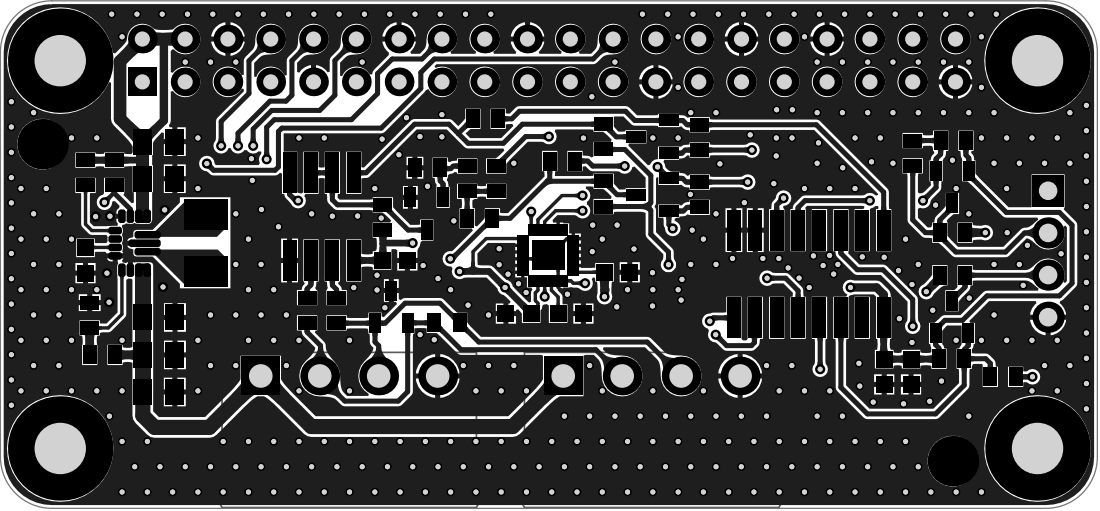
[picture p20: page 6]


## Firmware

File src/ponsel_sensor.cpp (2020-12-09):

#include <ponsel_sensor.h>


static bool init_done = false;
static pinout _pins;

static void pre_tran()
{
  digitalWrite(_pins.driver_en, _pins.enable_driver);
}

static void post_tran() 
{
  digitalWrite(_pins.driver_en, _pins.disable_driver);
}

void ponsel_sensor::rs485_board_init()
{
    //Prepare GPIO
    pinMode(_pins.driver_en, OUTPUT);
    pinMode(_pins.boost_en, OUTPUT);
    pinMode(_pins.uart_inh, OUTPUT);
    pinMode(_pins.uart_sel_a, OUTPUT);
    pinMode(_pins.uart_sel_b, OUTPUT);

    // Turn on 5V BOOST converter
    digitalWrite(_pins.boost_en, HIGH);

    // Drive INH low to enable MUX outputs, SEL A and B have to be low so
    // we are talking to uart 1, which leads to RS485 driver chip.
    digitalWrite(_pins.uart_inh,   LOW);
    digitalWrite(_pins.uart_sel_a, LOW);
    digitalWrite(_pins.uart_sel_b, LOW);
}

ponsel_sensor::ponsel_sensor(Stream &serial, 
                             uint8_t address, 
                             enum sensor_type type,
                             struct pinout pins)
{
    _serial = &serial;
    _address = address;
    _type = type;
    _measurements = {};
    _pins = pins;
}

bool ponsel_sensor::begin()
{
    uint8_t result;

    // Initialize water meter communication
    _sensor.begin(_address, *_serial);
    
    if (!init_done) {
        rs485_board_init();
        init_done = true;
    }

    _sensor.preTransmission(pre_tran);
    _sensor.postTransmission(post_tran);

    // Continiously pool for delay value, 
    // this can fail once, but it succeds afterwards

    for(int i = 0; i < 3; i++)
    {
      // Read one register from DELAY_ADDR
      result = _sensor.readHoldingRegisters(DELAY_ADDR, 1);

      if (result == _sensor.ku8MBSuccess) {
          _delay = _sensor.getResponseBuffer(0x00);
          return true;
      }
    }
    return false;
}

uint16_t ponsel_sensor::get_uint16_value(uint8_t index)
{
    return _sensor.getResponseBuffer(index);
}

float ponsel_sensor::get_float_value(uint8_t index)
{
    union convert {
        struct {
            uint16_t low;
            uint16_t high;
        };
        float f;
    }tofloat;

    tofloat.high = _sensor.getResponseBuffer(index);
    tofloat.low  = _sensor.getResponseBuffer(index + 1);

    return tofloat.f; 
}

void ponsel_sensor::print_measurements()
{
    if (_type == CTZN) {
        Serial.println("----------------------------------------------");
        Serial.print("Temperature:                    ");
        Serial.print(_measurements.param1);
        Serial.println(" °C");
        Serial.print("Conductivity CTZ:               ");
        Serial.print(_measurements.param2);
        Serial.println(" mS/ms");
        Serial.print("Salinity:                       ");
        Serial.print(_measurements.param3);
        Serial.println(" g/Kg");
        Serial.print("Conductivity CTZ no temp. comp: ");
        Serial.print(_measurements.param4);
        Serial.println(" mS/ms");
        Serial.println("----------------------------------------------");
    }
    else if (_type == OPTOD) {
        Serial.println("----------------------------------------------");
        Serial.print("Temperature:                    ");
        Serial.print(_measurements.param1);
        Serial.println(" °C");
        Serial.print("Oxygen:                         ");
        Serial.print(_measurements.param2);
        Serial.println(" %Sat");
        Serial.print("Oxygen:                         ");
        Serial.print(_measurements.param3);
        Serial.println(" mg/L");
        Serial.print("Oxygen:                         ");
        Serial.print(_measurements.param4);
        Serial.println(" ppm");
        Serial.println("----------------------------------------------");
    }
}

void ponsel_sensor::store_measurements()
{
    _measurements.param0 = get_uint16_value(0);
    _measurements.param1 = get_float_value(1);
    _measurements.param2 = get_float_value(3);
    _measurements.param3 = get_float_value(5);
    _measurements.param4 = get_float_value(7);
}

struct measurements ponsel_sensor::get_measurements()
{
    return _measurements;
}

bool ponsel_sensor::verfy_status_param()
{
    // 000: Measurement OK
    // 001: Measurement OK, but out of specifications
    // 010: Measurement OK with INFO 1
    // 011: Measurement OK with INFO 2
    // 100: Measurement impossible, out of specifications
    // 101: Measurement impossible with INFO 3
    // 110: Measurement impossible with INFO 4
    // 111: measurement under way (not yet available)
 
    // First param returned is status param
    uint8_t status = (_measurements.param0 >> 2) & 0x1;
    if (status == 0x1) {
        return false;
    }
    else {
        return true;
    }
}

bool ponsel_sensor::read_measurements()
{
        // Read 6 registers, status reg and plus 5 easurements 
        // 0x001F = 0b00111111
        _sensor.setTransmitBuffer(0, 0x001F);  
        
        // Write Transmit buffer to RUN_MEASURE_ADDR and write only one word
        uint8_t result = _sensor.writeMultipleRegisters(RUN_MEASURE_ADDR, 1);

        // Read 11 registers, one int and 5 floats, which is 11 bytes
        int read_reg_num = 11;

        // Required delay that we set begin method
        delay(_delay);

        result = _sensor.readHoldingRegisters(READ_MEASURE_ADDR, read_reg_num);

        if (result == _sensor.ku8MBSuccess) {
            store_measurements();
            verfy_status_param();
            return true;
        }
        else {
            return false;
        }
}

// calibration procedure
// Write '0x00000000 ' at 0x014C address and also 0x0001 at 0x004C address.

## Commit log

2020-10-29 Documentation in progress
    [ACCEL.SchDoc, MAIN.SchDoc, POWER.SchDoc, Pira-Smart-RS485-Addon.PcbDoc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]
2020-12-07 Changed the way the pins are assinned, added note about resistor change in README.
2020-12-17 Renamed ponsel to aqualabo
    [Digital sensor Frame_025_UK.xls]
2020-12-17 Added documentation about low current consumption
2020-12-17 Corrected the folder name
    [Digital sensor Frame_025_UK.xls]
